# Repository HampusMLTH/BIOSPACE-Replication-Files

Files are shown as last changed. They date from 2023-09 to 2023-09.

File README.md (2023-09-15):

# BIOSPACE Replication Files

Here are files for replicating BIOSPACE as documented in Månefjord, H., M. Li, C. Brackmann, N. Reistad, A. Runemark, J. Rota, B. Anderson, J. T. Zoueu, A. Merdasa and M. Brydegaard (2022). "A biophotonic platform for quantitative analysis in the spatial, spectral, polarimetric, and goniometric domains." Review of Scientific Instruments 93(11).

Reach out to me if something is missing or unclear

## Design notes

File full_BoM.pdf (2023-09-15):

Description | Supplier | Part # | Nbr | unit price | total cost
Display | | | 1
multimedia cable | | | 1
Mouse | | | 1
Keyboard | | | 1
Collimating lens | Edmund Optics | #45-508 | 1 $46,29 | $46,29
Imaging lens | Edmund Optics | #49-373 | 1 $121,82 | $121,82
Wire grid
polarizer | Edmund Optics | #48-544 | 2 $153,03 | $306,07
Hex. light pipe | Edmund Optics | #65-830 | 1 $117,80 | $117,80
LED 365 nm | Roithner Lasertechnik | UVLED-365-
2000-SMD | 1 $89,51 | $89,51
LED 405 nm | Roithner
Lasertechnik | smb1n-405v | 1 $14,94 | $14,94
LED 430 nm | Roithner
Lasertechnik | smb1n-430h | 1 $9,50 | $9,50
LED 490 nm | Roithner
Lasertechnik | smb1n-490h | 1 $10,42 | $10,42
LED 525 nm | Roithner
Lasertechnik | smb1n-525v | 1 $10,29 | $10,29
LED 630 nm | Roithner
Lasertechnik | smb1n-d630 | 1 $10,17 | $10,17
LED 810 nm | Roithner
Lasertechnik | smb1n-810d | 1 $12,97 | $12,97
LED 940 nm | Roithner
Lasertechnik | smb1n-940ds | 1 $16,63 | $16,63
BrickPi3 Core | Dexter Industries | - | 1 $119,81 | $119,81
Raspberry Pi 4b | Raspberry Pi
Foundation | - | 1 $70,48 | $70,48
CMOS camera | Basler | acA1920-
155um | 1 $900,27 | $900,27
Lego kit -
Bucket Wheel
Excavator | Brickshop | 42055 | 1 $609,11 | $609,11

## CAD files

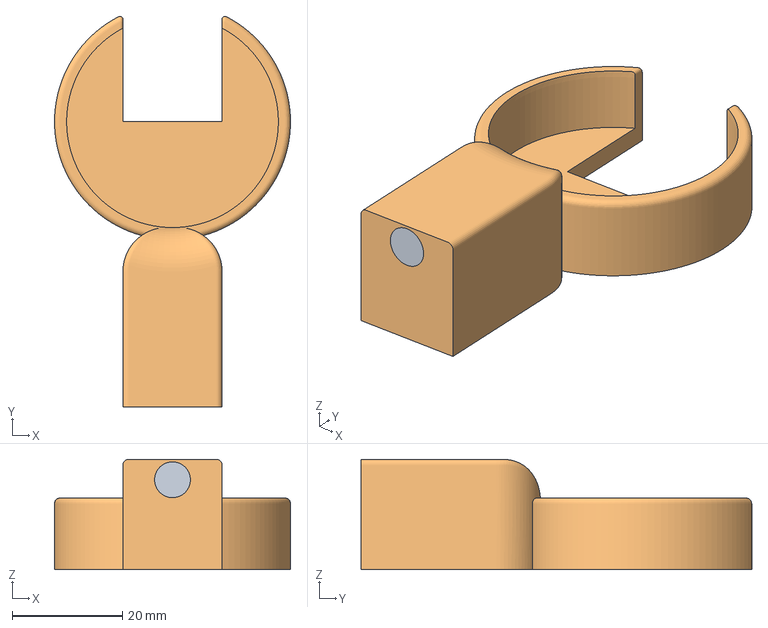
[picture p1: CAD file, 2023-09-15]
3D-print/refererence holder v4.3mf
42.8 x 70.8 x 20.0 mm

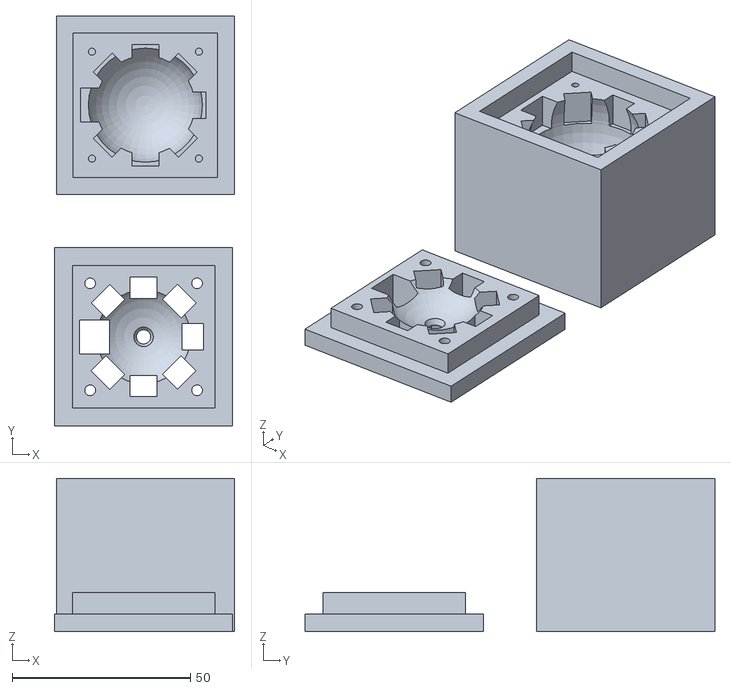
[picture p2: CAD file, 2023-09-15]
3D-print/LED_cavity.stl
50.5 x 115.0 x 43.0

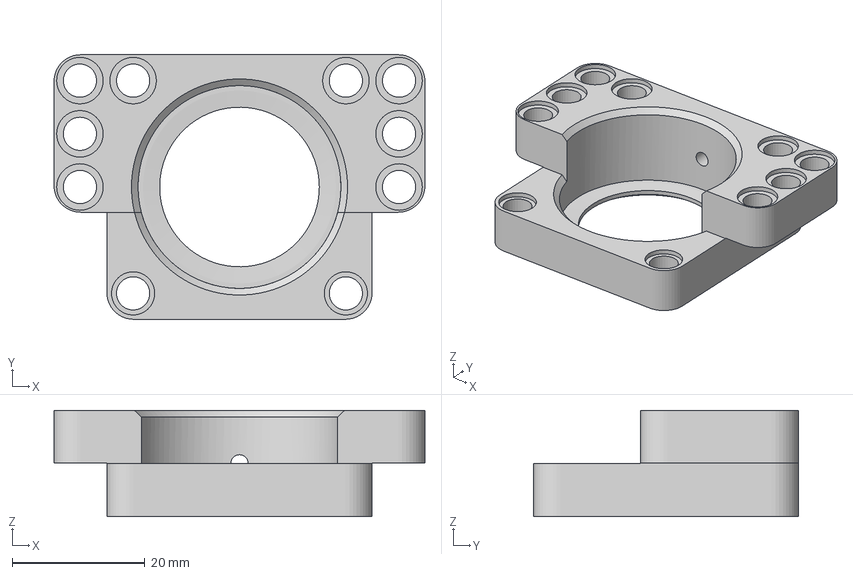
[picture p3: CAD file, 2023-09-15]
3D-print/AchromatHolder_v2.3mf
55.8 x 39.8 x 15.9 mm

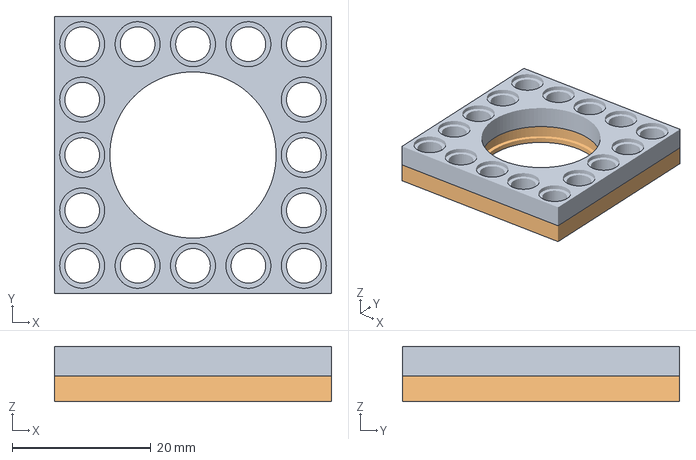
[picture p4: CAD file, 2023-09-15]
3D-print/lens_holder_D25mm_ET2mm43 v4.3mf
40.0 x 40.0 x 8.00 mm

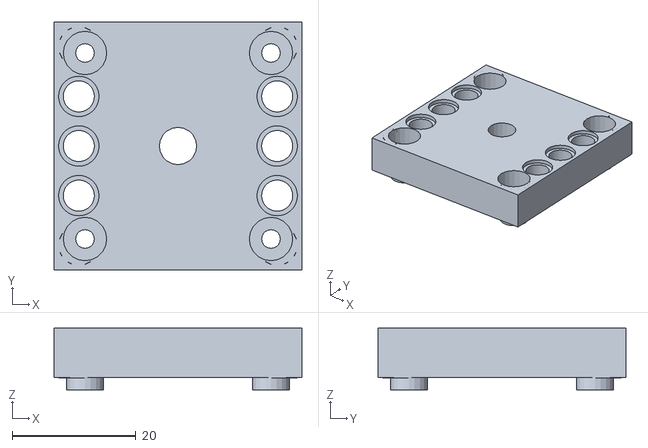
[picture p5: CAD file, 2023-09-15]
3D-print/pcb2lego mount.stl
40.0 x 40.0 x 10.00

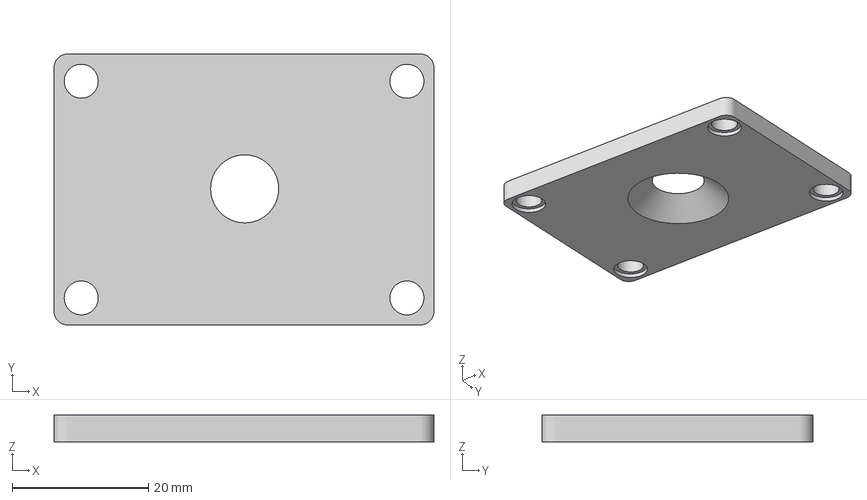
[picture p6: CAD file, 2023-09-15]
3D-print/iris10.3mf
55.8 x 39.8 x 3.95 mm

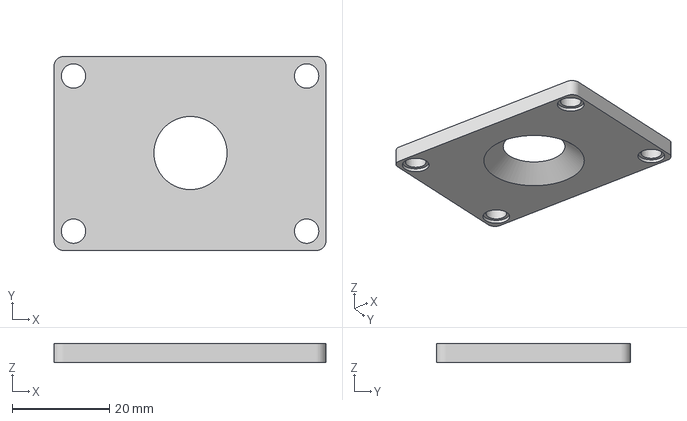
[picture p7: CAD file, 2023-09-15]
3D-print/iris15.3mf
55.8 x 39.8 x 3.95 mm

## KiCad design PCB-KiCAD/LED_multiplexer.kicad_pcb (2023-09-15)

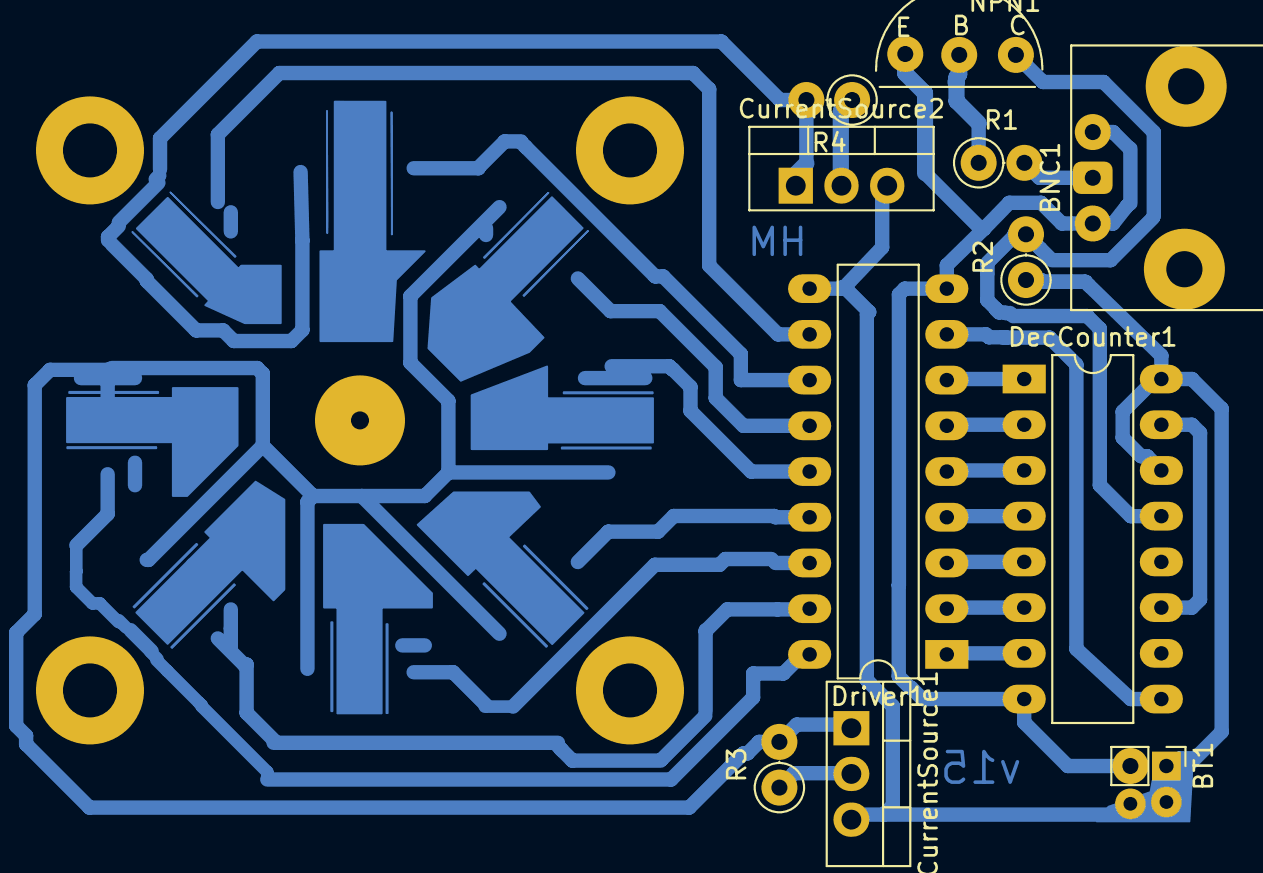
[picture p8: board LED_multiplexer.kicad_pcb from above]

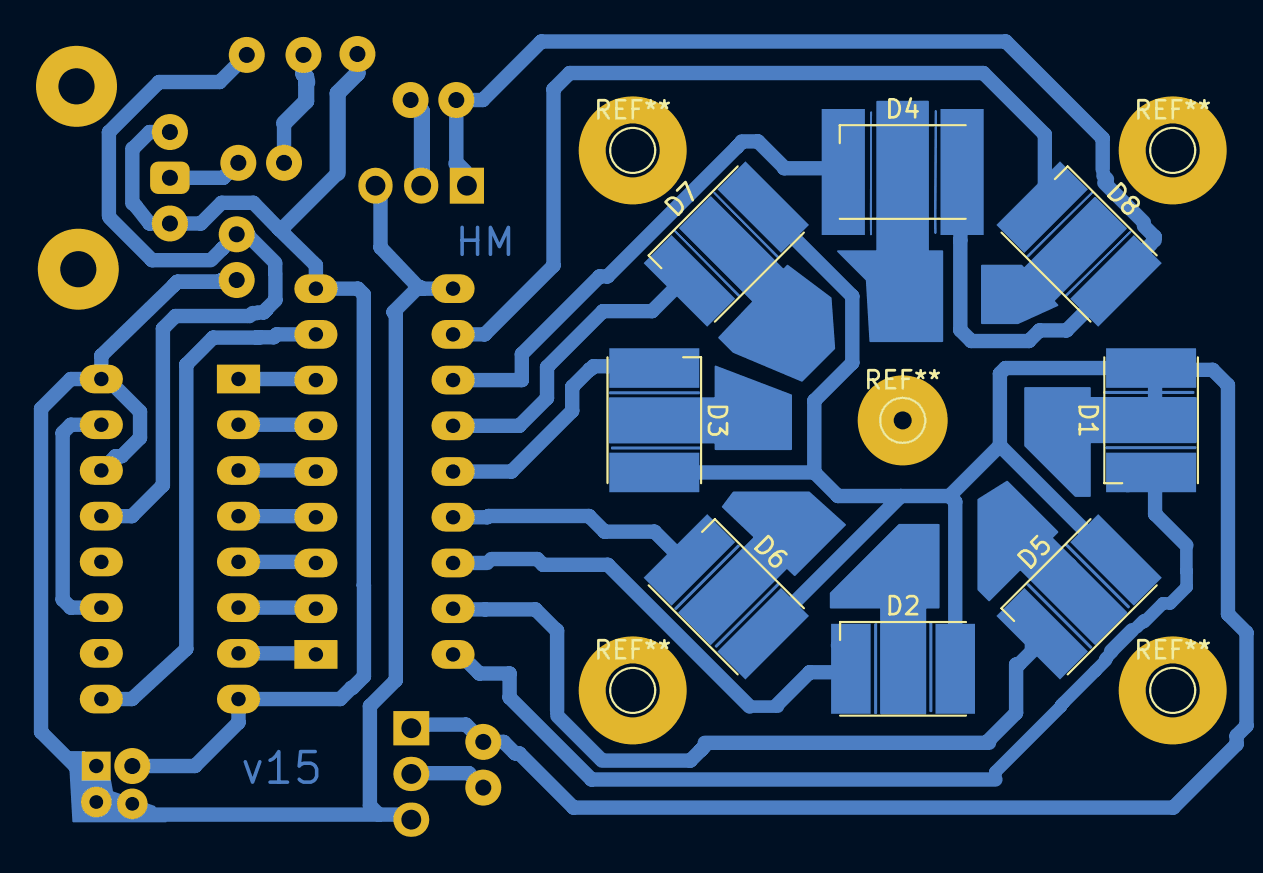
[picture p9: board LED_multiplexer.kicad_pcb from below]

Board: 2 copper layers, 19 parts (8 on the bottom side), 27 nets.

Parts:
BNC1: Coaxial; BNC_coax_Horizontal_c2
BT1: 9V; PinHeader_1x02_P2.00mm_Vertical_hampus
CurrentSource1, CurrentSource2: LM 317; TO-220-3_Vertical
D1: LEDs 365nm - 940nm; LED_SMB1N_5x5mm_sep_HS_right
D2, D3, D5, D6: LED; LED_SMB1N_5x5mm_sep_HS_right
D4: LED; LED_SMB1N_8x8mm_HS_left
D7, D8: LED; LED_SMB1N_5x5mm_sep_HS_left
DecCounter1: IC4017; DIP-16_W7.62mm_LongPads
Driver1: TBD62084A; DIP-18_W7.62mm_LongPads
NPN1: CMOS; pnp
R1, R2: 4k7; R_Axial_DIN0207_L6.3mm_D2.5mm_P2.54mm_Vertical
R3: 3.6; R_Axial_DIN0207_L6.3mm_D2.5mm_P2.54mm_Vertical
R4: 2.5; R_Axial_DIN0207_L6.3mm_D2.5mm_P2.54mm_Vertical

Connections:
GND: BNC1.2, BT1.2, DecCounter1.8, Driver1.9, NPN1.1
unnamed: BNC1.1, R1.1
unnamed: BT1.1, CurrentSource2.3
unnamed: CurrentSource1.1, D1.2, D2.2, D3.2, D5.2, D6.2, D7.2, R3.2
unnamed: CurrentSource1.2, R3.1
unnamed: CurrentSource2.1, D4.2, D8.2, R4.2
unnamed: CurrentSource2.2, R4.1
unnamed: D1.1, Driver1.18
unnamed: D2.1, Driver1.16
unnamed: D3.1, Driver1.14
unnamed: D4.1, Driver1.12
unnamed: D5.1, Driver1.17
unnamed: D6.1, Driver1.15
unnamed: D7.1, Driver1.13
unnamed: D8.1, Driver1.11
unnamed: DecCounter1.1, Driver1.7
unnamed: DecCounter1.2, Driver1.6
unnamed: DecCounter1.3, Driver1.5
unnamed: DecCounter1.4, Driver1.4
unnamed: DecCounter1.5, Driver1.3
unnamed: DecCounter1.6, Driver1.2
unnamed: DecCounter1.7, Driver1.1
unnamed: DecCounter1.9, Driver1.8
unnamed: DecCounter1.10, DecCounter1.15
unnamed: DecCounter1.13, NPN1.3, R2.2
unnamed: NPN1.2, R1.2
VCC: CurrentSource1.3, DecCounter1.14, DecCounter1.16, Driver1.10, R2.1

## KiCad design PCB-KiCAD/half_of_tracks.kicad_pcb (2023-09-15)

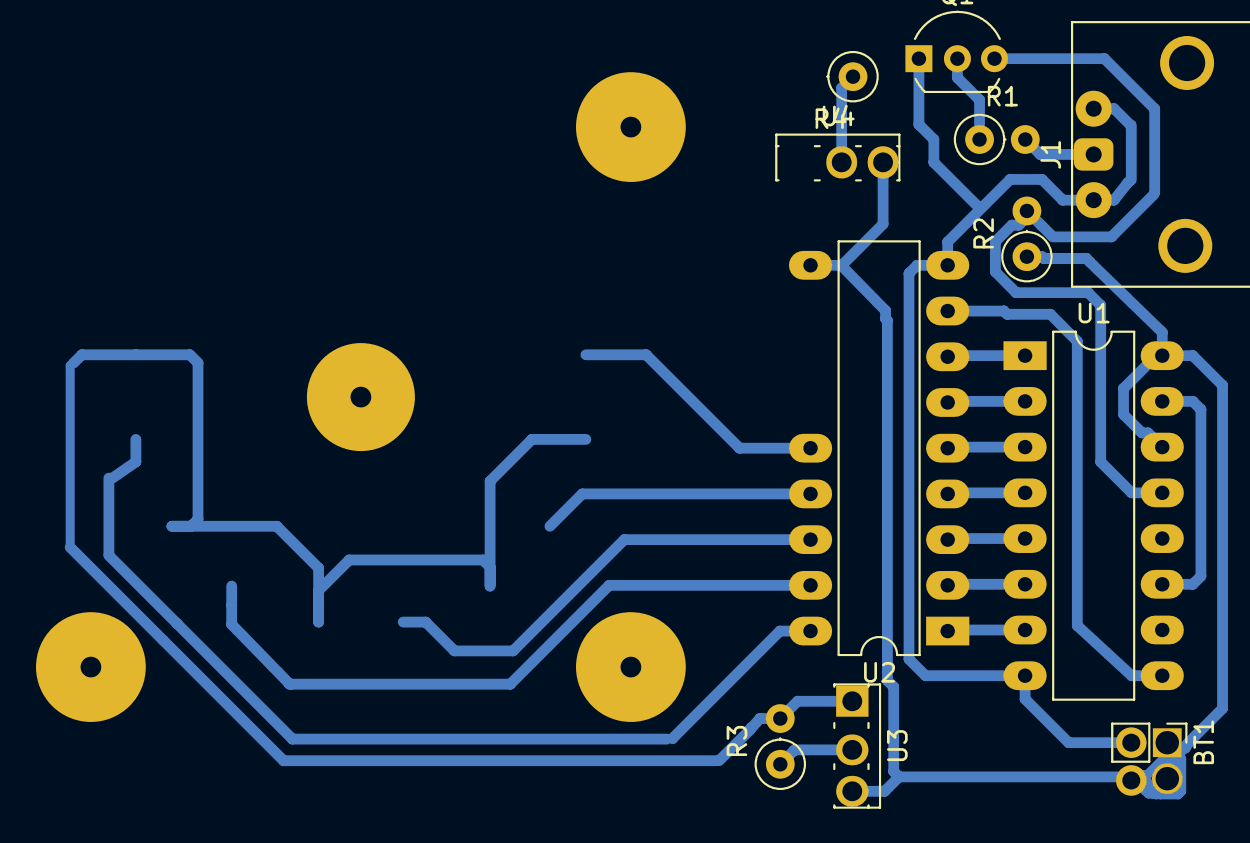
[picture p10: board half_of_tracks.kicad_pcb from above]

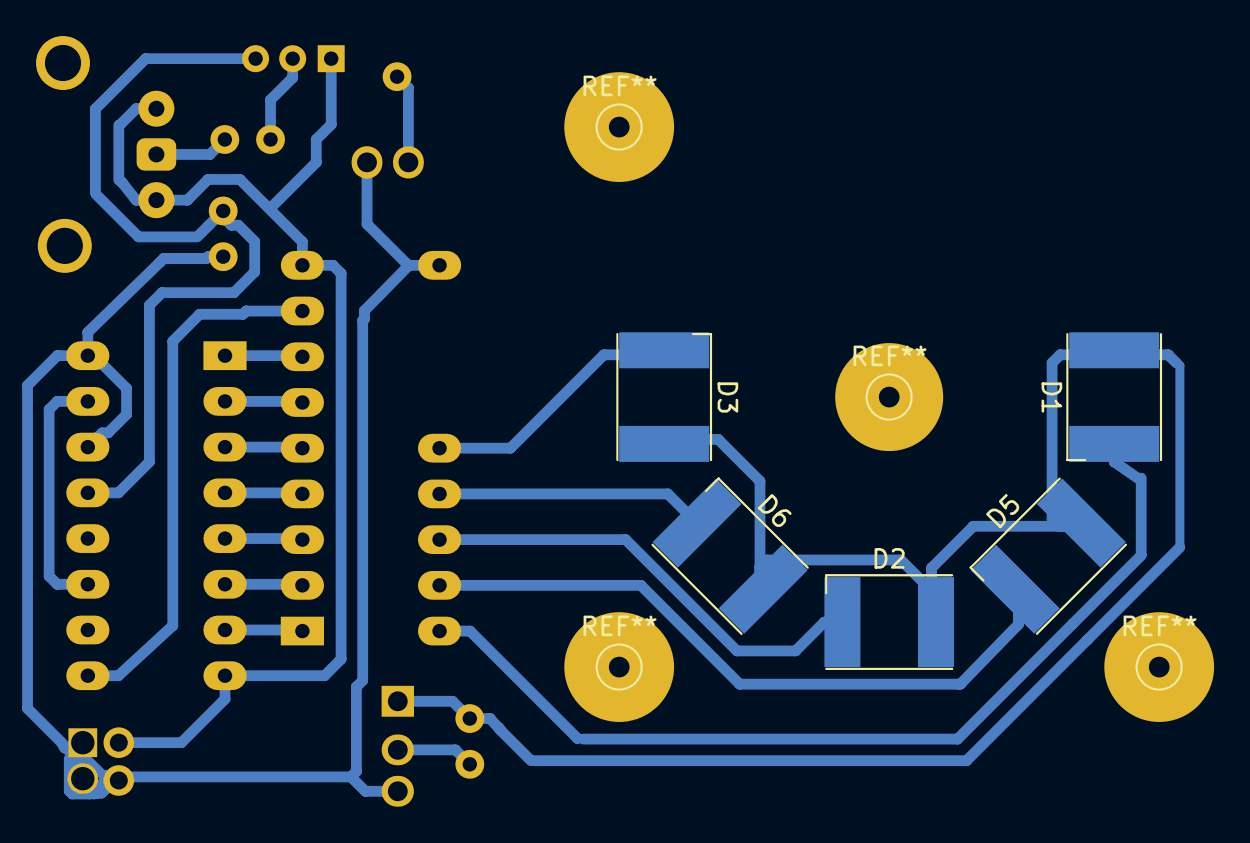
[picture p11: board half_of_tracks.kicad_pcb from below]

Board: 2 copper layers, 16 parts (5 on the bottom side), 22 nets.

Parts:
BT1: 9V; PinHeader_1x02_P2.00mm_Vertical_hampus
D1, D2, D3, D5, D6: LED; LED_SMB1N_5x5mm2
J1: Conn_Coaxial; BNC_coax_Horizontal_c2
Q1: 2N2219; NPN_tht_Inline_4mm2
R1, R2: 4k7; R_Axial_DIN0207_L6.3mm_D2.5mm_P2.54mm_Vertical
R3: 3.6; R_Axial_DIN0207_L6.3mm_D2.5mm_P2.54mm_Vertical
R4: 2.5; R_Axial_DIN0207_L6.3mm_D2.5mm_P2.54mm_Vertical_half
U1: IC4017; DIP-16_W7.62mm_LongPads
U2: TBD62084A; DIP-18_W7.62mm_LongPads_half
U3: LM317L_TO92; LM317
U4: LM317L_TO92; LM317_half

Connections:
GND: BT1.2, J1.2, Q1.1, U1.8, U2.9
unnamed: D1.1, U2.18
unnamed: D1.2, D2.2, D3.2, D5.2, D6.2, R3.2, U3.1
unnamed: D2.1, U2.16
unnamed: D3.1, U2.14
unnamed: D5.1, U2.17
unnamed: D6.1, U2.15
unnamed: J1.1, R1.2
unnamed: Q1.2, R1.1
unnamed: Q1.3, R2.2, U1.13
unnamed: R3.1, U3.2
unnamed: R4.1, U4.2
unnamed: U1.1, U2.7
unnamed: U1.2, U2.6
unnamed: U1.3, U2.5
unnamed: U1.4, U2.4
unnamed: U1.5, U2.3
unnamed: U1.6, U2.2
unnamed: U1.7, U2.1
unnamed: U1.9, U2.8
unnamed: U1.11, U1.15
VCC: BT1.1, R2.1, U1.14, U1.16, U2.10, U3.3, U4.3

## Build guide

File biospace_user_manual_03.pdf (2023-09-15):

V03

Hampus Månefjord | LUND UNIVERSITY

## BIOSPACE User Manual

Hampus Månefjord

Department of Physics, Lund University

March 20, 2022

This document contains instructions for the biophotonics platform BIOSPACE. Contact us at:

hampus.manefjord@forbrf.lth.se

mikkel.brydegaard@forbrf.lth.se

## Contents

## Instrumentation overview

The instrument consists of a multispectral light source; optical elements for imaging a biological target;

a mechanical structure with four degrees of freedom for rotation; a hardware control interface; and an

application controlling the data acquiring process. An overview of the instrument is presented in Fig.1.

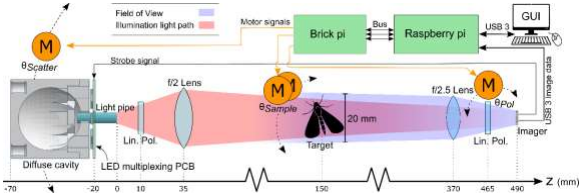
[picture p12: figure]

Fig. 1. Block diagram of hardware control interfaces and schematic drawing of optical components.

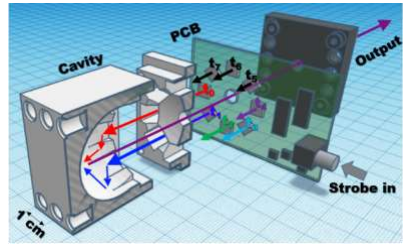
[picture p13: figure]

Fig. 2. A schematic drawing based on a CAD of the LED multiplexer with a white diffusive cavity displaying its functionality

The light source is a LED multiplexor with a white, diffusive cavity seen in Fig. 2. The LED multiplexor is made of some basic electronic components including LEDs with 8 different wavelengths (365 – 940 nm) that are strobed one at a time in different time slots. A camera synchronized with the LEDs captures each image which together form a multispectral image.

The instrument’s mechanical parts are based on Lego and 3D-printed parts. The sample can be rotated in two degrees of freedom: the “yaw” and “aspect” angles. Further a polarization filter can be rotated and the angle of light incidence on the sample can be controlled with the “scatter angle”. These angles are seen in Fig. 3.

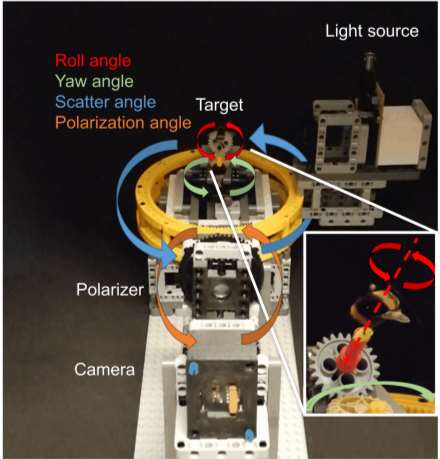
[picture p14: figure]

Fig. 3. Motorized degrees of freedom of the movements of the platform includes scatter angle, polarization angle, aspect angle and yaw angle.

## Hardware

## 2.1. Electronics components

List of hardware includes:

- Raspberry pi 4b
- Brickpi board 3
- Camera: Basler Ace acA1920-155um
- 3 units of EV3 lego servo motors
- USB3 Hard drive
- Display/Monitor
- Keyboard
- Mouse
- Custom Multiplexing PCB

Cables:

- 3 units of 50cm EV3 cables
- Basler GP-I/O Cable, HRS 6p/open
- MicroHDMI cable
- Coaxial BNC cable
- 9V 4.44A power supply

- 18V 1A power supply

Connect as follows:

- Assemble the BrickPi3 case according to https://www.dexterindustries.com/BrickPi/brickpi3-getting-started-step-1-assembly/ (https://www.dexterindustries.com/BrickPi/brickpi3-getting-started-step-1-assembly/)
- The keyboard and mouse are connected to the USB2 ports of the Raspberry pi
- The hard drive and the camera are connected to the USB3 ports of the Raspberry pi
- The display/monitor are connected to the Raspberry pi through the microHDMI port
- The Brickpi 3 is placed on the 40-pin GPIO header of the Raspberry pi
- The 3 lego motors are connected to the Brickpi through lego EV3 cables
- The Brickpi is supplied with 9V
- The PCB is connected to the Strobe-out of the camera with a Basler GP-I/O Cable, HRS 6p/open to coaxial BNC
- The PCB is supplied with 18V

See the bill_of_materials.pdf for full list of components.

## 2.2. 3D-printed components

The 3D printed components are compatible with Lego Technic and includes:

- Cavity for diffusing the LED light
- Print with 100% infill with white ABS/PLA filament
- for optimal UV performance apply some BaSO4-coating to the inside of the cavity
- Lens adaptor
- Camera adaptor
- PCB adaptor

Print all adaptors with black filament (100% infill is not necessary)

If you are using the Dremel 3D45 for 3D-printing, use the software Dremel Digilab 3D slicer

Select medium (0.2mm) or higher profile quality, chose infill (eg 100% or 20% depending on the piece) have Generate support unticked, but build plate adhesion ticked.

Generate a file and load in onto the printer with a USB memory stick.

## 2.3. PCB

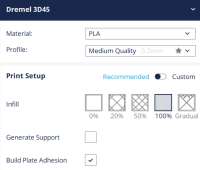
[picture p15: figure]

The PCB is driving the LEDs one at the time, synchronized with the camera. There are attached electrical schema, PCB-layout file, and a ready-to-run (setting may vary depending on router) gcode file with the routing pattern for milling the PCB.

If you are making the PCB yourself with a CNC-mill see the document PCB_making_workflow.pdf

## 2.4.Lego Assembly

Lego prices needed are found in the

- Bucket-wheel-excavator kit
- 4 EV3 motors
- 4 EV3 cables

Instructions for assembly are found in the file Lego_assembly_Instructions_for_BIOSPACE.pdf

## Installing software

Operating system

Flash SDcard of the raspberry pi by following the guide at

https://www.dexterindustries.com/howto/install-raspbian-for-robots-image-on-an-sd-card/

with biospace_install\2020-02-13-raspbian-buster-full.img

Move the SDcard to the raspberry pi and boot

You can set the time with terminal input

Brickpi

Testfiles are located at /home/pi/Dexter/BrickPi3/Software/Python

More info at https://www.dexterindustries.com/BrickPi/brickpi3-getting-started-step-4-program-brickpi-robot/brickpi3-getting-started-program-python/ (https://www.dexterindustries.com/BrickPi/brickpi3-getting-started-step-4-program-brickpi-robot/brickpi3-getting-started-program-python/)

Camera software

Install by

Run the software

sudo date -s "Jul 5 08:10"

sudo dpkg-reconfigure tzdata

sudo dpkg -i pylon_6.X.XX.XXXXX-deb0_amd64.deb

/opt/pylon/bin/pylonviewer curl -kL dexterindustries.com/update_brickpi3 | bashkpy

sudo reboot

More info at https://github.com/strawlab/flydra/wiki/Basler-Pylon-for-Linux-backend

Camera – python interface

find correct version of whl file:

Your responses might differ. Find the corresponding .whl file at https://github.com/Basler/pypylon/releases

and download

install pypylon:

or equivalent.

## Operation

Place your sample on a pin, with some adhesive/blu tack or on a 3D-printed sample holder. Some modification to the setup might be necessary depending on the size of the sample

Test motors

After connecting motors according to section 2, run the python programs

move_roll_angle.py

move_yaw_angle.py

move_scatter_angle.py

and make sure the specified motor rotates. The number of degrees to be moved by each script can be modified by editing the code in each file.

Test camera

For testing, start the pylonviewer software to get a stream from the camera. You do that by opening a terminal and writing:

uname –a

- armv7l

python3 –V

- cp37

pip3 install pypylon-1.5.1-cp37-cp37m-linux_armv7l.whl

/opt/pylon/bin/pylonviewerApp

Here you can adjust camera setting such as exposure time until you get an image of your sample.

To test the multiplexing PCB connect its BNC coax to the GPIO of the camera. The use the setting

Output

Line 3

Exposure active

And connect the multiplexing PCB to a 18V power supply.

Adjust the camera distance from the lens until it is in focus.

If you will use multiple aspect/yaw angles of your sample, you can rotate it and make sure is still in the field of view of the camera for all relevant rotations.

Now you need to define your measurement protocol which is a series of angles and exposure times. One row of the protocol spreadsheet is executed at a time

Roll | Yaw | Scatter

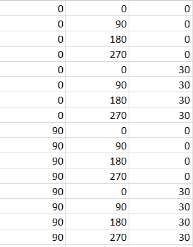
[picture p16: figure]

In this example protocol file there will be 16 measurements, first the yaw angle of the sample will be rotated a complete revolution, then the roll will be rotated, and a new revolution of the aspect angle will be captured. Next the same procedure will be done again but with a new scatter angle and exposure time.

You then find the acquisition code in biospace_code/ biospace_main.py

The program can be run as any python script, e.g., with Thonny.

To make a measurement:

1. Have a defined protocol of relevant positions
2. Move the instrument into a starting position.
3. Turn off (or down) the room lighting.
4. Start the measurement GUI.
5. power on the instrument light source.
6. Press start camera in the GUI. The light source should now cycle through the different colored LEDs, and it performs a calibration to find the timeslot with all LEDs turned off.
7. After a few cycles - press “start measurement”. A text “MEASURING” will be in the GUI while the measurement is ongoing.

After you have done your measurement make sure to load and look at the files to make sure you have captured what you need, and not, e.g., underexposed or overexposed all images.

There will be 8 images for each row in the protocol file so possibly a lot of images to look at. So there is also a spreadsheet output to get an overview of how many overexposed pixels there are in each image.

## Reading and visualizing data

The program captures images, saves them in a folder named after the instrument angles, and names the tiff files according to the illumination wavelength. E.g. the path for an image could be “..\scatter_60_yaw_10_roll_0\365_nm.tiff”.

Images can be analyzed using any program that can read tiff files, e.g. Matlab.

Load the image in Matlab the with

A matrix of intensity values between 0 and 1 is loaded, in double precision. The acquisition program has before saving the images subtracted the background signal and converted the images from 12 bit unsigned integer to double.

The values need to be corrected for the emission intensity of the LEDs. That is done by dividing the intensity values with the values from an image of a white calibration target illuminated with the same emission wavelength.

A color image is displayed by concatenating three images representing red, green and blue such as

There are some Matlab scripts available for reading the images and doing some simple visualization.

Start with the file biospace_main.m

Good luck!

img_630nm=imread(‘\scatter_60_yaw_10_roll_0\630_nm.tiff’);

img_630nm = img_630nm/mean(mean(calibration_img_630nm));

color_img= cat(3,img_red, img_green, img_blue); imagesc(color_img);
